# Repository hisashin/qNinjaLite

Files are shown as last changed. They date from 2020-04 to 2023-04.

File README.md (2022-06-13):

# Open Source $50 qLAMP machine qNinja



# $300 Real Time PCR and LAMP machine "[qNinja](https://github.com/hisashin/qNinja)" is also available



## Reference Links
- [qNinja portal](https://qninja.hisa.dev)

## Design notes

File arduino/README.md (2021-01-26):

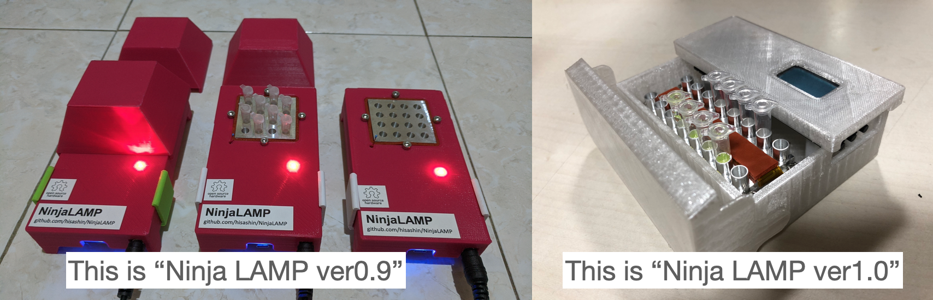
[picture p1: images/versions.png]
versions


The configuration for each version can be found in HardwareConf.cpp and HardwareConf.h.
HardwareConf class has two construction methods for two models:

* ver0.9 (initFirstModel)
* ver1.0 (initLCDModel)

Pins, thermistors, PID constants and some model-specific properties for NinjaLAMP's basic functionalities are defined in HardwareConf::initFirstModel() function.

## ver0.9

ver0.9 has no dedicated user interfaces. It sends values every 250　milliseconds by serial communication.
The values can be plotted by the serial plotter of Arduino IDE. This process is implemented in the loop function.

## ver1.0

In April, ver0.9 was released just after a week of rapid prototyping by @hisashin and @maripo. Now @hisashin upgraded its PCB and 3d model  to ver1.0 with widely used [Seeeduino Xiao](https://wiki.seeedstudio.com/Seeeduino-XIAO/), [I2C SSD1306 LCD](https://www.aliexpress.com/item/33028828291.html?spm=a2g0s.9042311.0.0.26274c4dPiM0Ki), [I2C 2kb EEPROM](https://www.digikey.com/en/products/detail/stmicroelectronics/M24C02-RMN6TP/2038677) and 3 tact switches.
- [Hardware updrade is done (2020 Nov 10)](https://www.facebook.com/hisakawa/posts/10158727487954481)
- [New Package (2020 Nov 6)](https://www.facebook.com/hisakawa/posts/10158717794254481)
- [New PCB (2020 Oct 28)](https://www.facebook.com/hisakawa/posts/10158696375544481)
- [KiCad](https://github.com/hisashin/NinjaLAMP/tree/master/kicad/NinjaLAMP)
- [3d model](https://gallery.autodesk.com/projects/149287/ninjalamp)

NinjaLAMP will get following benefits from this upgrade.

- **Standalone** : No need to be connected to PC anymore. LCD displays all informations and we can choose menu by tapping switches as up/down/ok buttons.
- **Programmable** : We can configure custom temperature profiles with switches and store them in EEPROM.
- **Manufacture Friendly** : PCB supports [Seeed PCBA](https://www.seeedstudio.com/prototype-pcb-assembly.html) service and here is their quotation. All electric parts are included and soldered except $1.66 LCD and $0.46 thermistor. With $10 heater and $10 tube holder, NinjaLAMP can be manufactured less than $40. That's great advantage for screening mass poplulation.

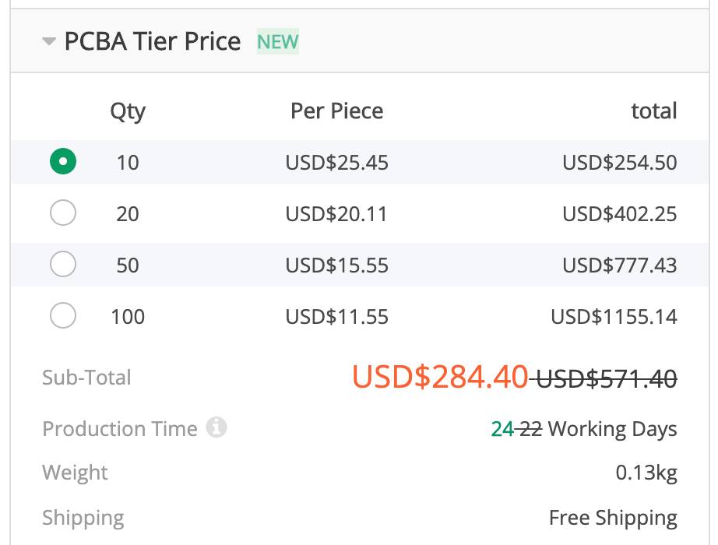
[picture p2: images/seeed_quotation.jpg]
seeed_quotation


### Pin assignment

* LED_R : PA02_A0_D0
* LED_G : PA04_A1_D1
* LED_B : PA10_A2_D2
* HEATER : PA11_A3_D3
* SDA : PA08_A4_D4_SDA
* SCL : PA09_A5_D5_SCL
* AIN_AIR : PB08_A6_D6_TX
* TACT2 : PA06_A10_D10_MOSI
* TACT1 : PA05_A9_D9_MISO
* TACT0 : PA07_A8_D8_SCK
* AIN_WELL : PB09_A7_D7_RX

---

**For Valerio**

## How to Setup IDE and test ver1.0

* Connect NinjaLAMP to your computer with USB TypeC cable. No need to connect 12V AC adapter at first.
* NinjaLAMP ver1.0 uses [Seeeduino XIAO](https://wiki.seeedstudio.com/Seeeduino-XIAO/)(not AVR but SAMD21). Follow their **[Software Step 1 to 5](https://wiki.seeedstudio.com/Seeeduino-XIAO/#software)**
* Upload **"File > Examples > 01.Basics > Blink"** to NinjaLAMP. Orange LED next to USB connector will start blinking.
* Go to **Sketch-> Include Library-> Manage Libraries**, search "ssd1306" and install Alexey Dynda's **[ssd1306 library](https://github.com/lexus2k/ssd1306)**.

* Add "NinjaLAMPCore" library to the build environment. Choose **Sketch > Add .ZIP Library...** and select **NinjaLAMP/arduino/lib/NinjaLAMPCore.zip**.

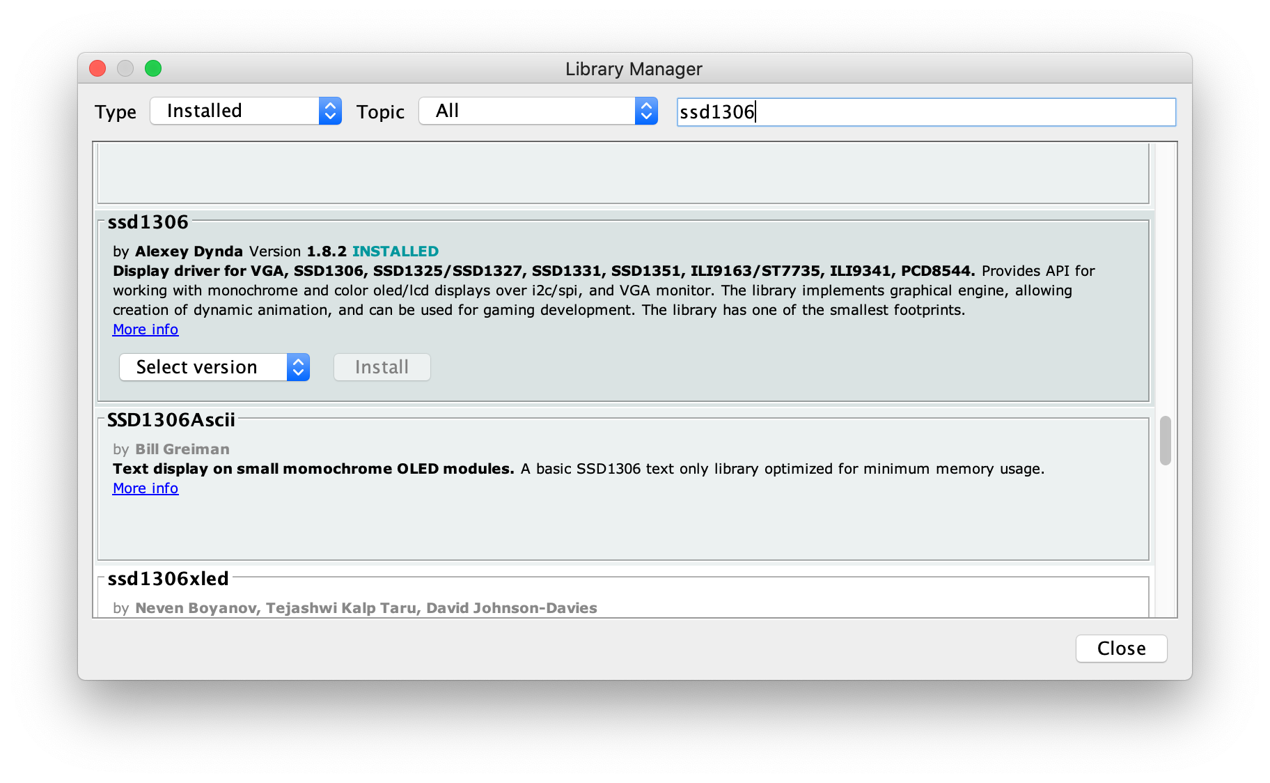
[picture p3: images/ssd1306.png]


* Restart Arduino IDE
* Upload **"File > Examples > ssd1306 > demos > ssd1306_demo"** to NinjaLAMP. I2C LCD displays [demo](https://github.com/lexus2k/ssd1306/blob/master/examples/demos/ssd1306_demo/ssd1306_demo.ino).
* Clone this NinjaLAMP respository to somewhere
* Upload [NinjaLAMP/arduino/examples/xiao_example_gpio](https://github.com/hisashin/NinjaLAMP/tree/master/arduino/examples/xiao_example_gpio)
* Click magnifying glass icon at the top-right corner and set rate to "9600 baud"
* Tap switches to change values. If adapter is connected, tube holder will be heaten. Be careful.

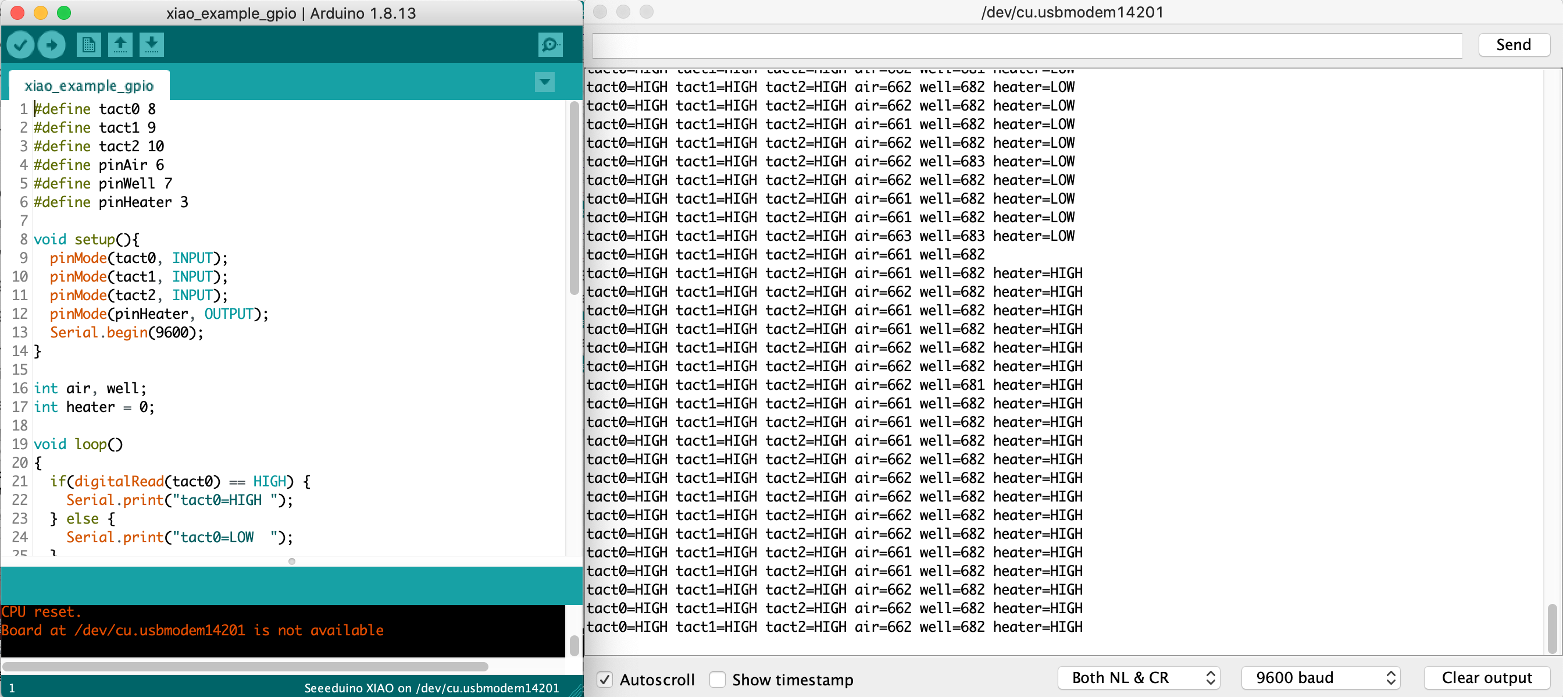
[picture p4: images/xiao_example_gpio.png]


* Upload [NinjaLAMP/arduino/examples/xiao_example_eeprom](https://github.com/hisashin/NinjaLAMP/tree/master/arduino/examples/xiao_example_eeprom)
* Click magnifying glass icon at the top-right corner and set rate to "9600 baud"
* Program writes 0x32(=50) at address 0 of EEPROM on board with writeI2CByte(). Then readI2CByte() read the value of the same address.

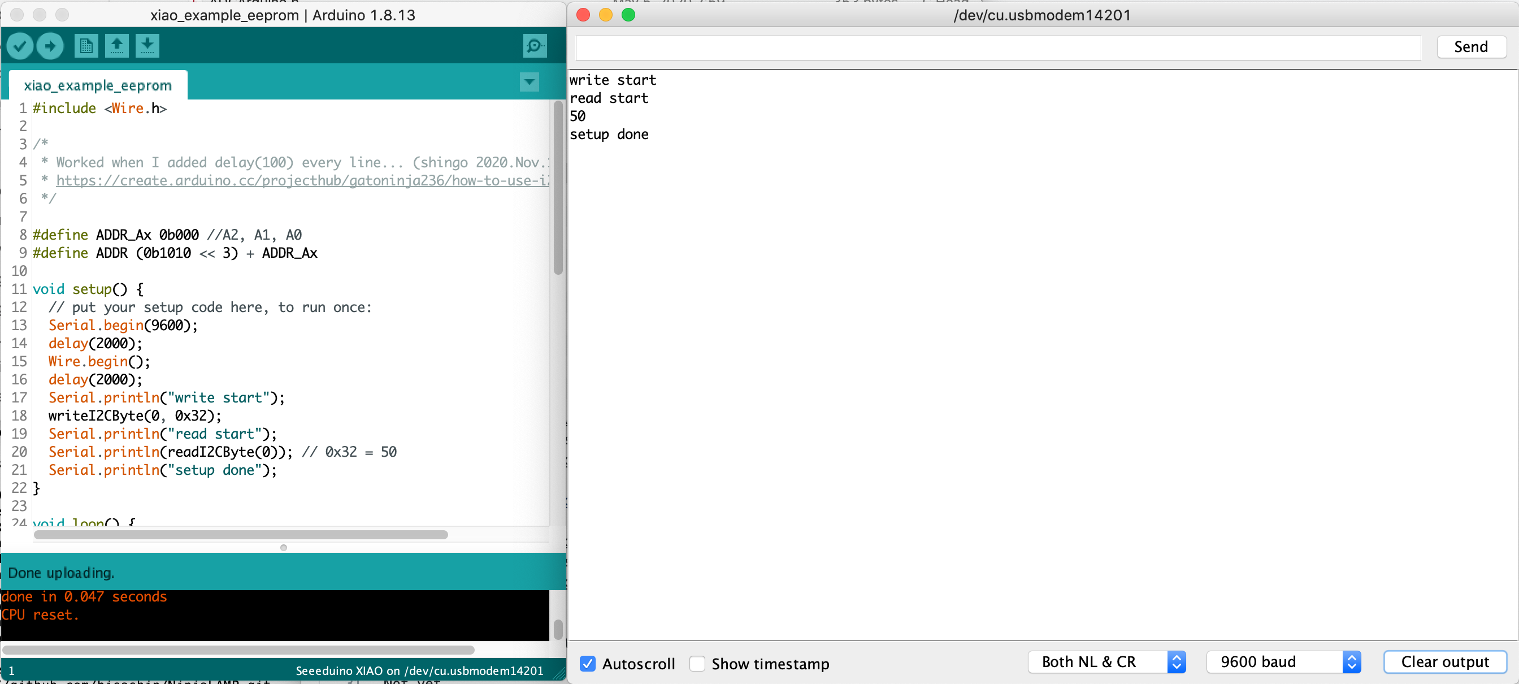
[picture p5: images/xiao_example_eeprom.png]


* Change (address, value) from (0, 0x32) to another. You can confirm its's saved correctly.

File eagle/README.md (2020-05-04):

*Schematic*
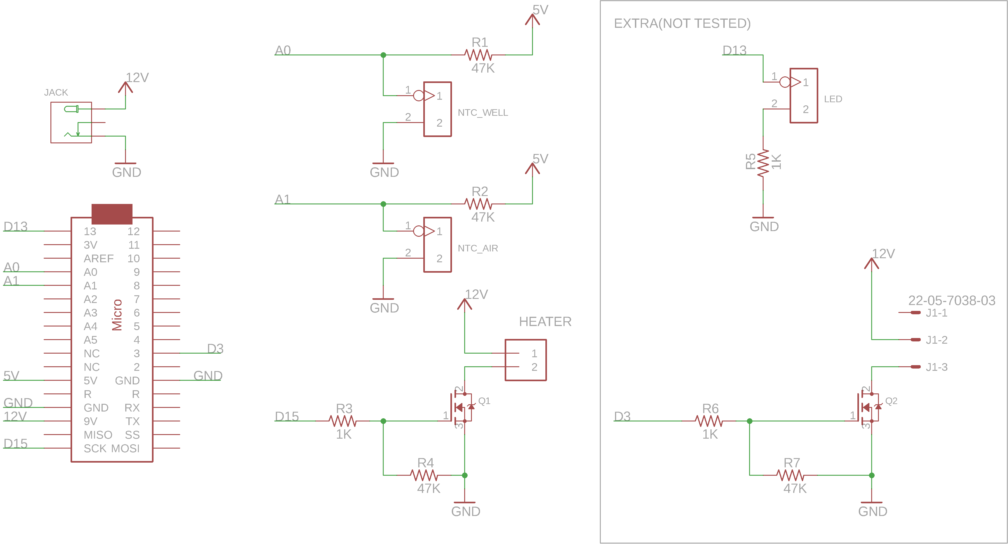
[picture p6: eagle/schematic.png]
Schematic schematic


*Layout for PCB*
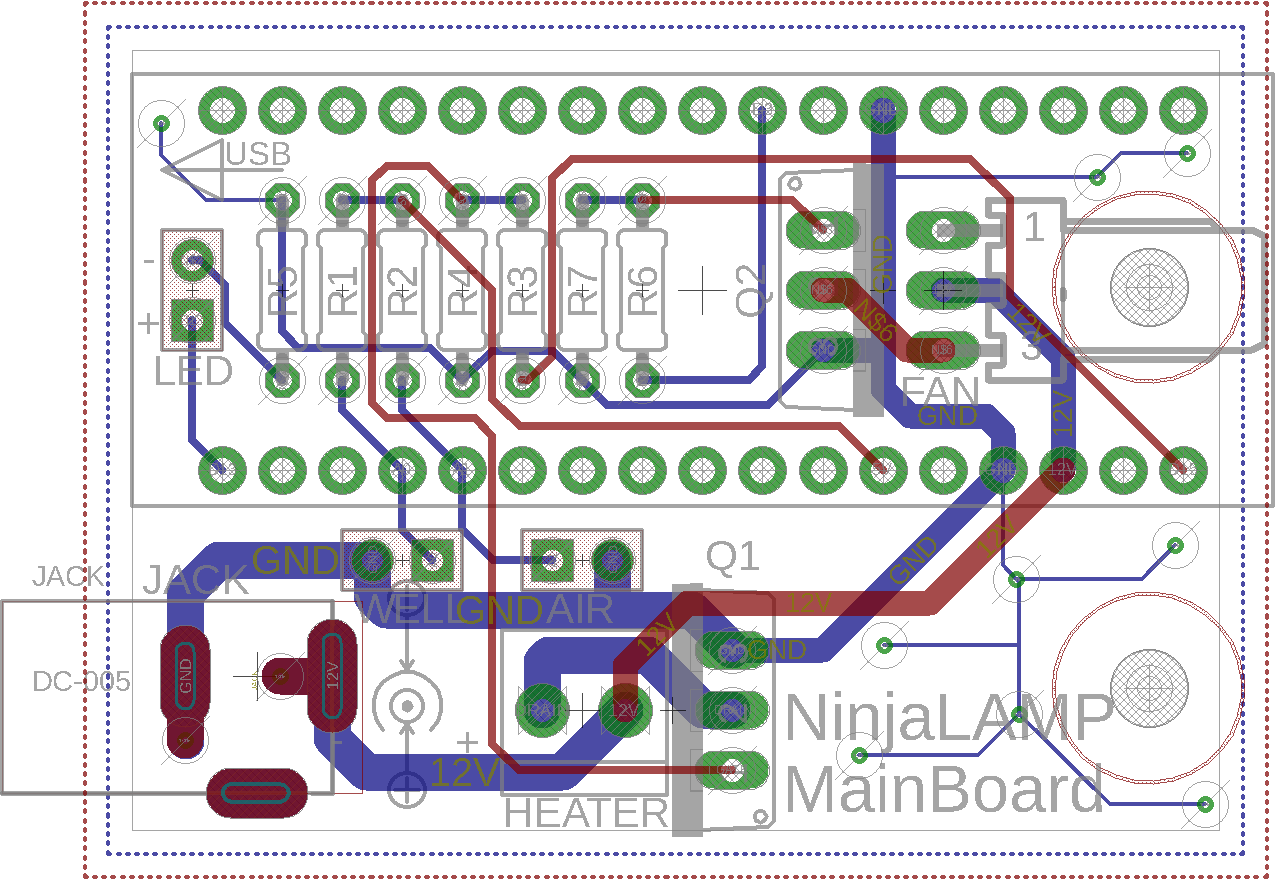
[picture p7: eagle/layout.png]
Layout layout


*Layout for hand wiring*
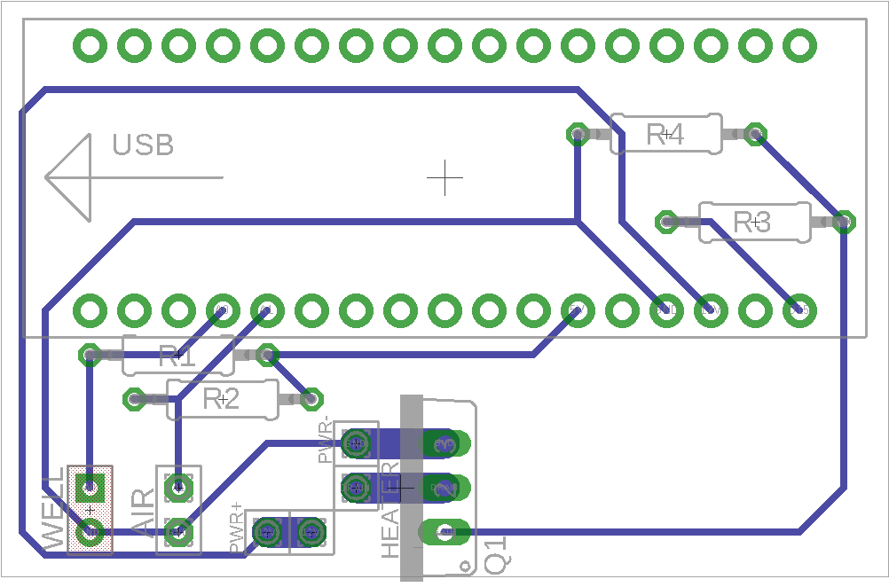
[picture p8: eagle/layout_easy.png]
LayoutEasy layout_easy


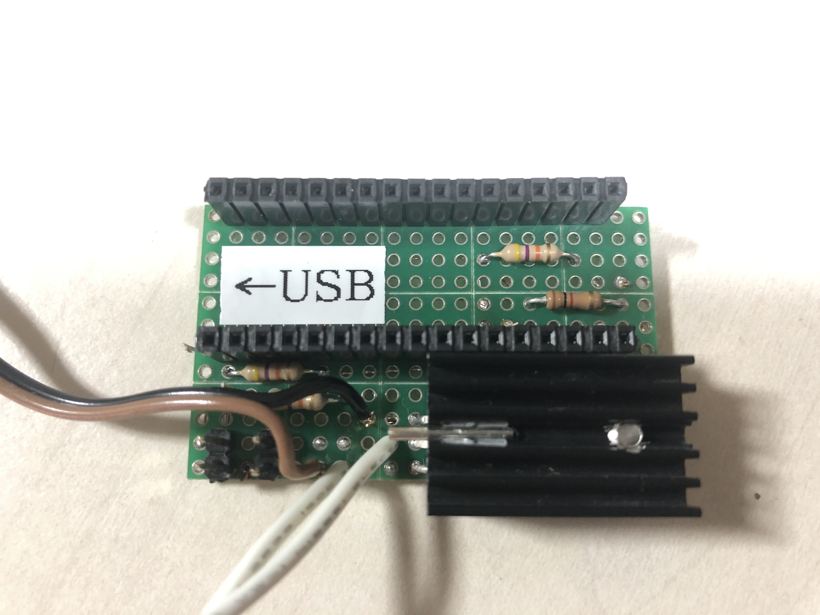
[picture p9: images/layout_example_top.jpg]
hand1

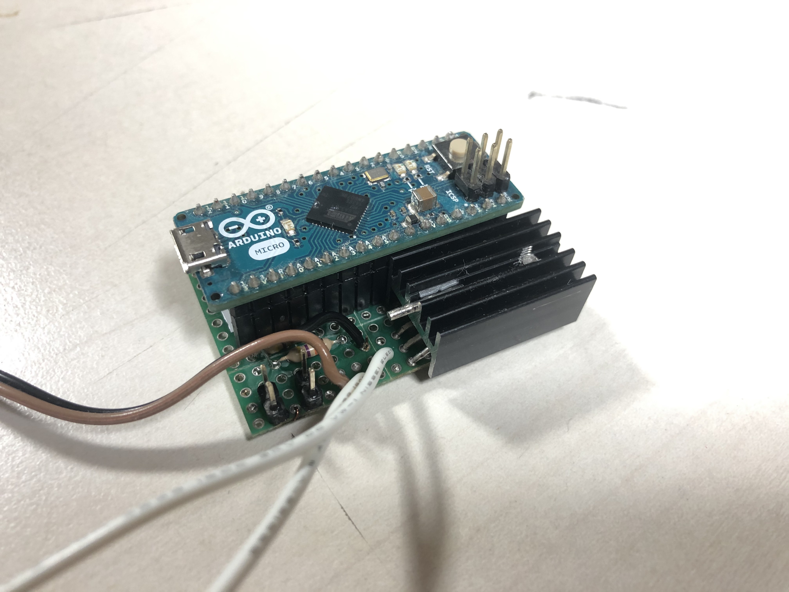
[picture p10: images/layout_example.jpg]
hand2

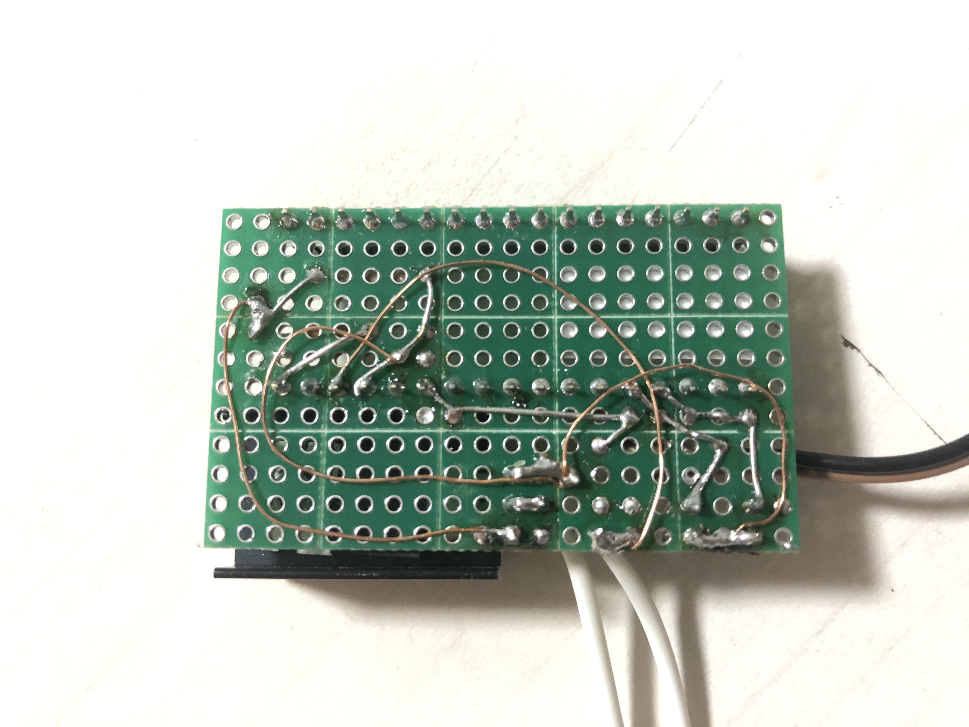
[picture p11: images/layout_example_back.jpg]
hand3


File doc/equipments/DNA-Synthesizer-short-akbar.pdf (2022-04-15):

# OVERVIEW OF DNA PRIMER PRODUCTION LINE

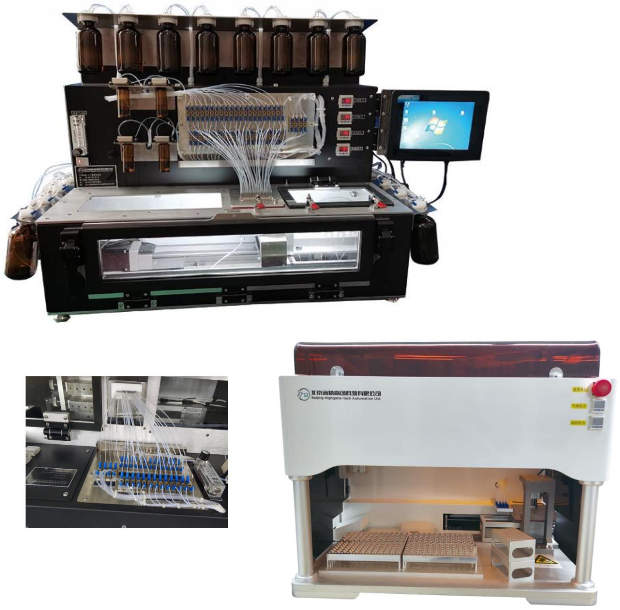
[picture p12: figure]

BY NUR ARKBAR AROFATULLAH, S.P., M.BIOTECH., PH.D.

DNA PRIMER PRODUCTION LINE

DNA primer is single stranded DNA used to prime the polymerase chain reaction. The single stranded DNA is produced synthetically using DNA synthesizer. Typical process used in synthetically creating DNA is the phosphoramidite method. This method is replicated in the 3'- to 5'- direction which is opposite to that in nature on a column containing solid supporting material. The typical solid support for DNA synthesis is Polysterene (PS) and Controlled Phore Glass (CPG). One amidite base is added per synthesis cycle on solid support. When the sequence is completed phosphoramidite, the DNA is separated from the solid support and the base protecting groups are removed. Further post synthesis process is required until the synthetic DNA can be used as PCR primer.

A. THE COMPLETE CYCLE FOR DNA SYNTHESIS INCLUDE:

### 1. Reagent Preparation

Dilution of Phosphoramidite Base Powder to the desired concentration suitable for DNA synthesis. Can be done with dissolver instrument to avoid Oxygen contamination.

### 2. DNA synthesis

a. Detritylation
Detritylation is the removal of protecting (blocking) group Dimethoxytrityl (DMT) from phosphoramidite base. DMT prevent the 5'-end from reacting with anything. Detritylation is typically done with Trichloroacetic Acid (TCA) or Dichloroacetic Acid (DCA) in Dichloromethane. DCA is preferable for longer DNA synthesis due to weaker acid, however the process is slower (60 sec). For faster DNA synthesis (usually shorter DNA), TCA is preferable (35 sec). Longer exposure to acid can cause depurination/mutation.
b. Activation
After DMT is removed, an amidite base (A-C-G-T) is dissolved in Acetonitrile (ACN) and mixed with activator solution Tetrazole or Ethylthiotetrazole (ETT). The activator protonates the 3'-end to facilitate reaction with 5'-end of the oligo.
c. Oligonucleoside coupling on solid support
- Universal solid support: Solid support column with the linker only, without any nucleoside attached.
- Standard support: Solid support with the first nucleoside already attached
d. Capping
To prevent the extension of DNA sequence that did not react in the coupling step, the remaining 5'-hidroxyl group must be blocked with a mixture of two capping solution known as CAP-A (Acetic Anhydride) and CAP-B (N-Methymidazole). This also allows for easier purification in post synthesis
e. Oxidation
The bond of the attached amidite base is strengthened trough iodine oxidation to prepare for the next step of detritylation. Backbone modifications be done as a replacement for the oxidation step.
The Oxidizer:
- Iodine and H2O
- Pyridine
- Tetrahydrofuran
f. Washing
After the oxidation step a wash of Acetonitrile (ACN) is run through the line before the next detritylation. Another wash step is also performed after detritylation.

B. POST DNA SYNTHESIS

Once the DNA sequence is completed, the oligo must undergo post synthesis operation in order to become biologically active
a. Cleavage
The first step to post synthesis is to separate the finished oligo from the solid support. Cleavage is done with strong bases Ammonium Hydroxide, Methylamine, or AMA (a mixture of Ammonium Hydroxide and Methylamine)
b. Deprotection
The second step requires removing the amidite base protecting group from the oligo by raising temperature to 70 – 90 °C.
c. Oligo quantification
- Nanodrop
- Qubit Assays
- Epoch Microplate reader (for batch quantification)
Overview of Post synthesis operation: Cleave + Elute -> Deprotection -> Oligo Quantification
D. PRICE LIST OF REAGENT AND CONSUMABLES FOR DNA SYNTHESIS
No. | Reagents & Consumables | MOQ | Price (USD)
1. | Trichloroacetic Acid (TCA) | 4 Liter | 35
2. | Phosphoramidite base - A/T/G/C | 5 grams | 22.5
3. | Acetonitrile | 4 Liter | 33
4. | Tetrazole or Ethylthiotetrazole | 4 Liter | 106
5. | CAP-A (Acetic Anhydride) | 4 Liter | 82
6. | CAP-B (N-Methymidazole) | 4 Liter | 92.5
7. | Iodine | 4 Liter | 86
8. | Ammonium Hydroxide | 1 Liter | 60
9. Reverse phase silica column - | C18 (price/bag) | 1 bag (100 pcs) | 160
10. CPG column HJ-Z-12-100 | 100nmol (price/bag) | 1 bag (1000 pcs) | 160
11. | Filter | 100 | 160
12. | Molecular trap(10g/piece) | 100 | 950
13. | Molecular trap(5g/piece) | 100 | 785

E. THE REQUIRED MACHINERY FOR PRODUCING DNA PRIMER:
1. Amidites Dissolver Instrument (Step 1)

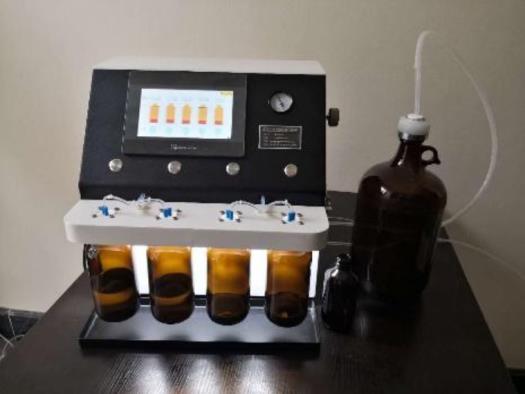
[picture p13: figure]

2. 12 DNA synthesizer (Step 2 a,b,c,d,e, f)

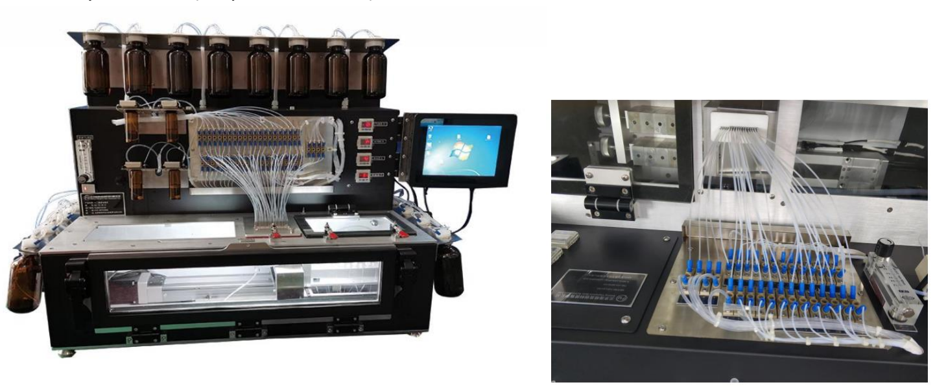
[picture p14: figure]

TECHNICAL SPECIFICATION
No | Parameter | HJ 12-Channel Synthesizer
1. | Synthesis column | 12
2. | Number of amidite inlet | 16
3. | Number of reagent inlet | 7
4. | Synthesis range | 25 nmol – 300 µmol
5. | Synthesis rate | 4-6 Coupling/minutes
6. Total time for 20-unit Poly-T | synthesis | 2 h 30 min
7. Total solvent (acetonitryl) | consumption per coupling | 2.6 mL
8. | Coupling efficiency | 99% (60 base, 50nmol)
9. | CPG feed | CPG in Pre-packed column
10. | Availability of DMT monitoring * | Yes
11. | Production scale (weekdays) | 500-600 primer tube/month
*DMT carbocation absorbs at 495 nm and thereby produces an orange color that can be used to monitor coupling efficiency.

3. Ammonolysis instrument (Step 3 a,b)

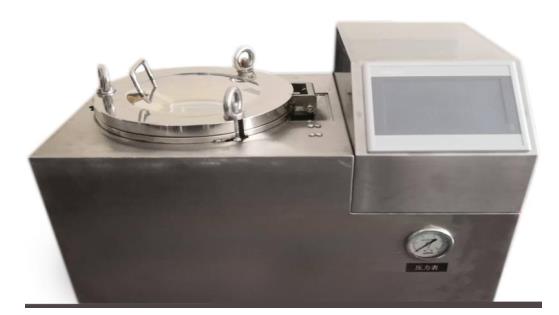
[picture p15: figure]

4. Nanodrop/Qubit/Epoch Microplate reader (Step 3 c)

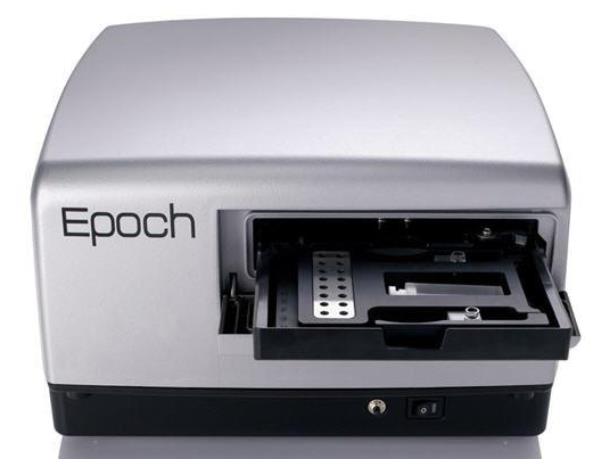
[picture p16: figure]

5. Pipetting workstation (Optional)
The Pipetting workstation with the function of Elution and purification, this workstation uses for different step in the synthesis cycle, because it has different function in one.

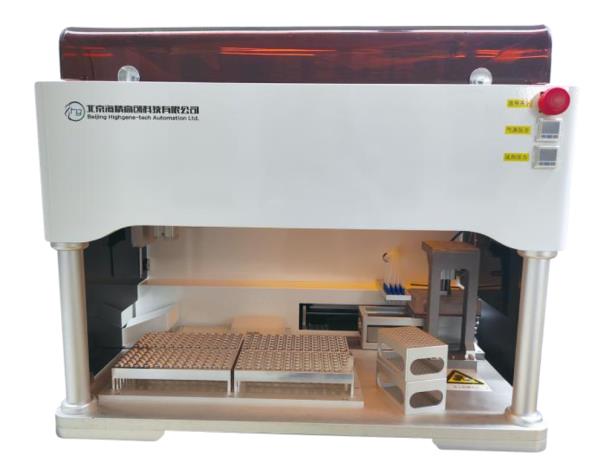
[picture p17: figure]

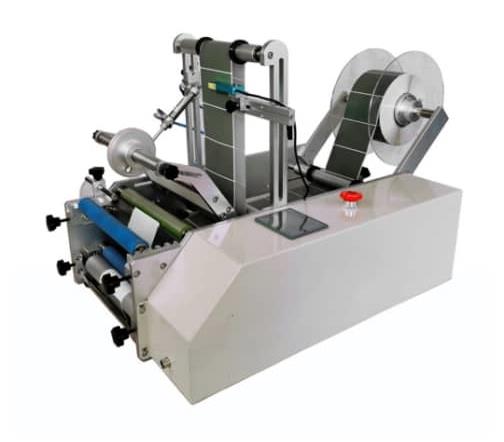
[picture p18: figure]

6. Tube Labeling Machine

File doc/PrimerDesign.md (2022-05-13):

[ApE](https://jorgensen.biology.utah.edu/wayned/ape/) for general primers (and occationall TaqMan probes)

[IDTs quest](https://eu.idtdna.com/pages/tools/primerquest) for qPCR TaqMan assay.

It is basically a cut down and more user friendly version of [Primer3](https://primer3.ut.ee/)

It also provides cheap primers($4 per primer for 25nm) and probes($100).

[NEBs](https://lamp.neb.com/) for LAMP assays

EvaGreen or Sybr Green when using dyes for LAMP or qPCR (if not using probes)

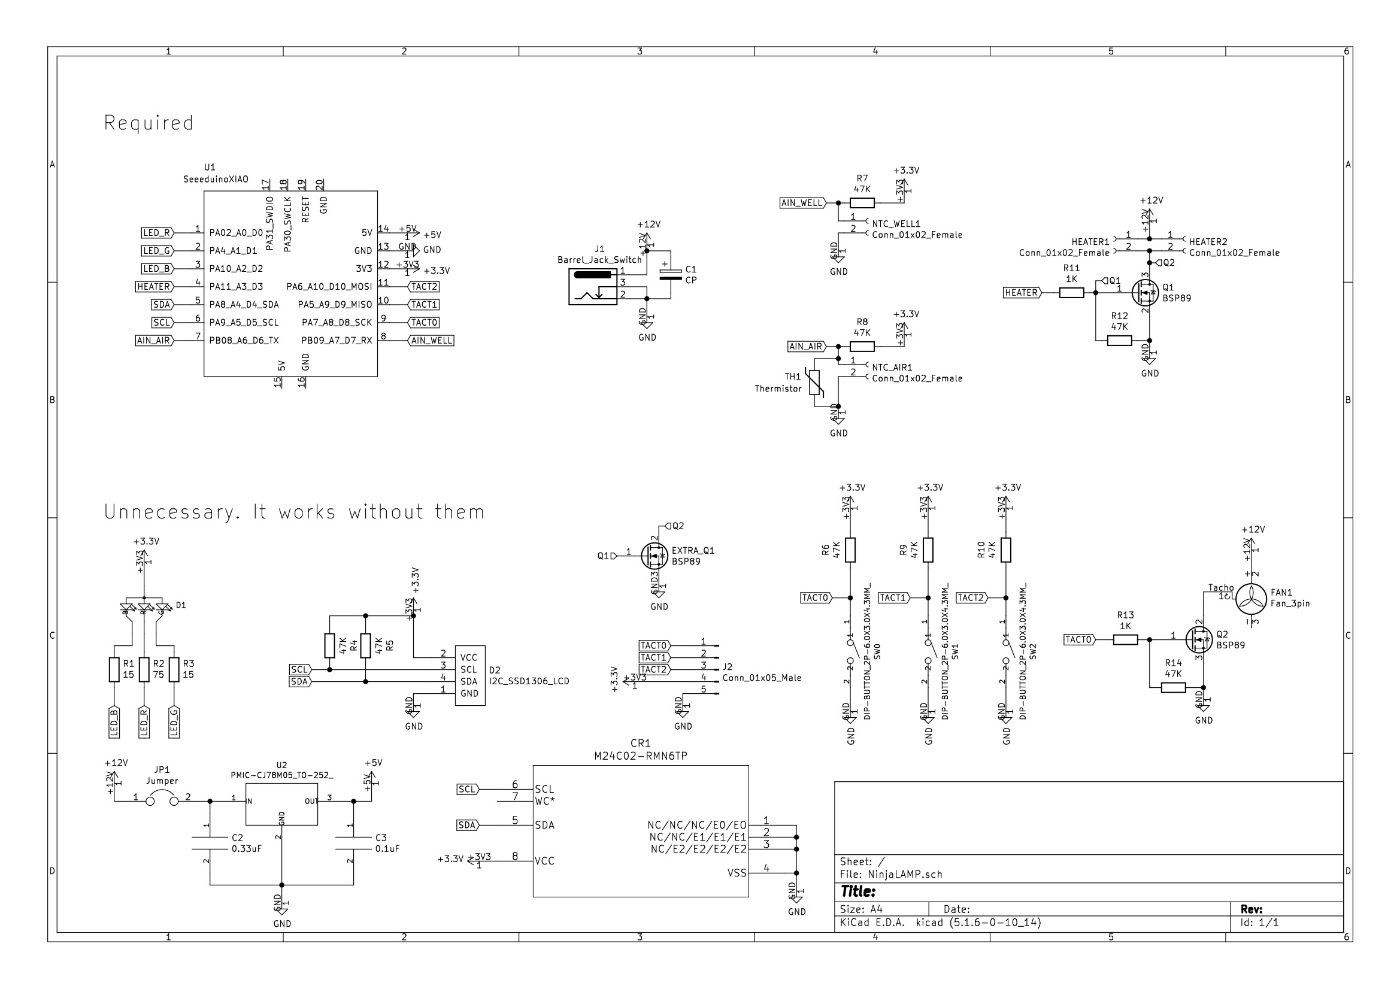
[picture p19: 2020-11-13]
kicad/NinjaLite/ver1.0/schematic.jpeg

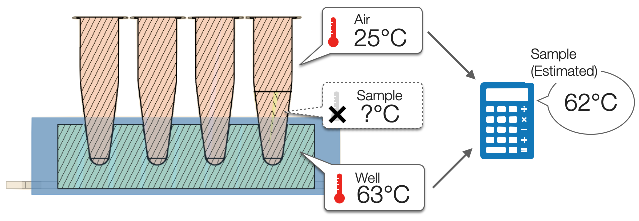
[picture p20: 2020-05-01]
images/heat_simulation/illustration_s.png

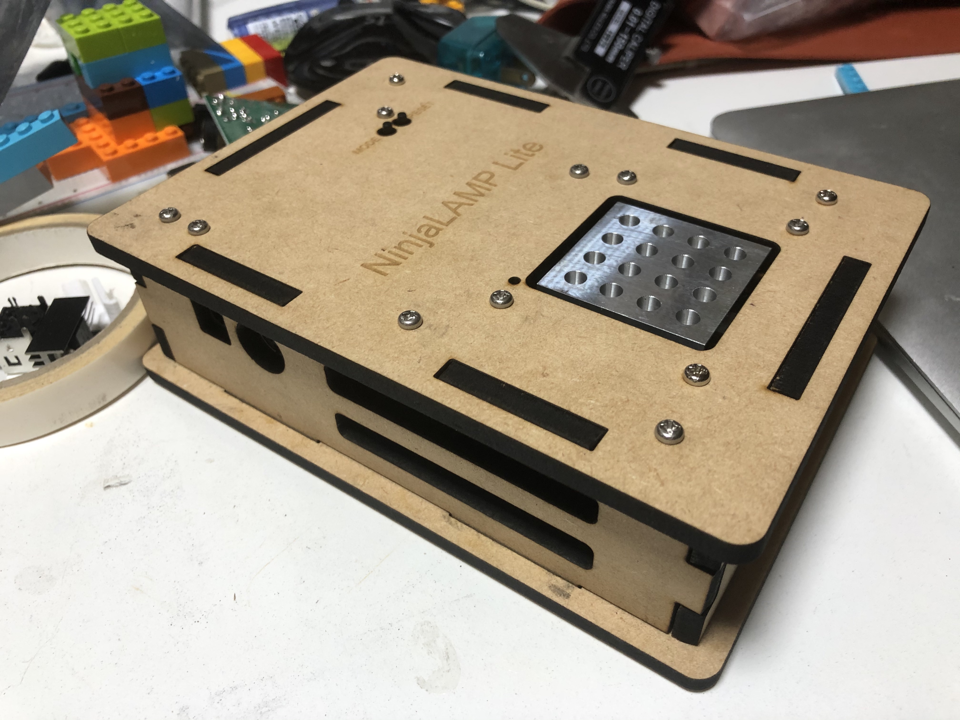
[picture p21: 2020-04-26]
images/lite_outside.jpg

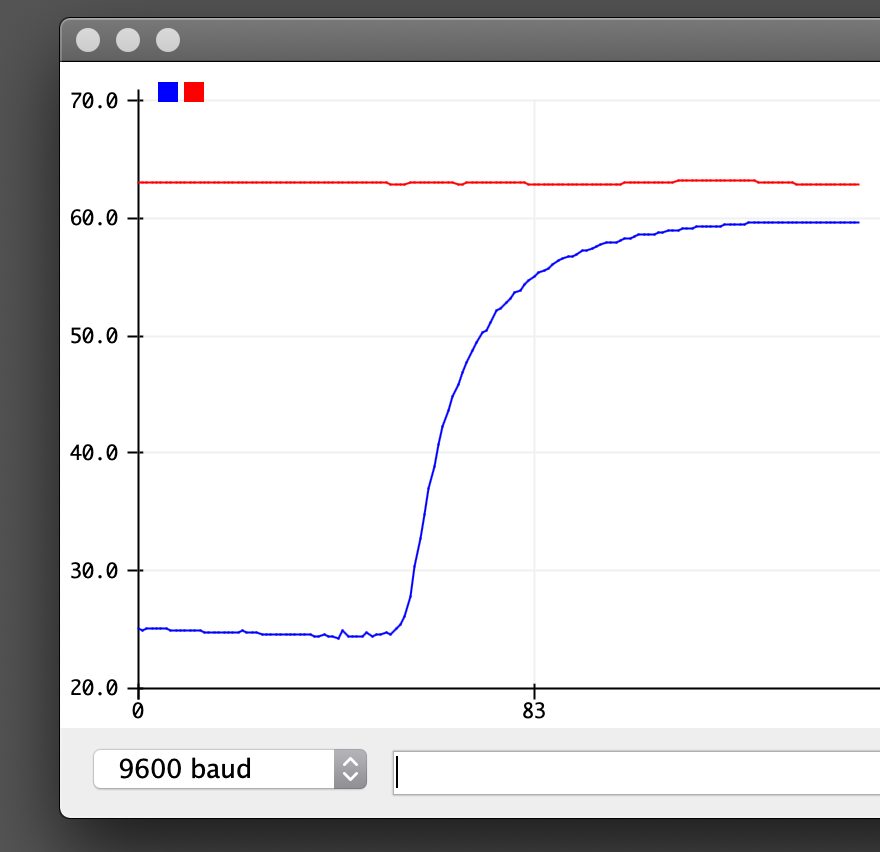
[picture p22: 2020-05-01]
images/heat_simulation/plot_heating.png

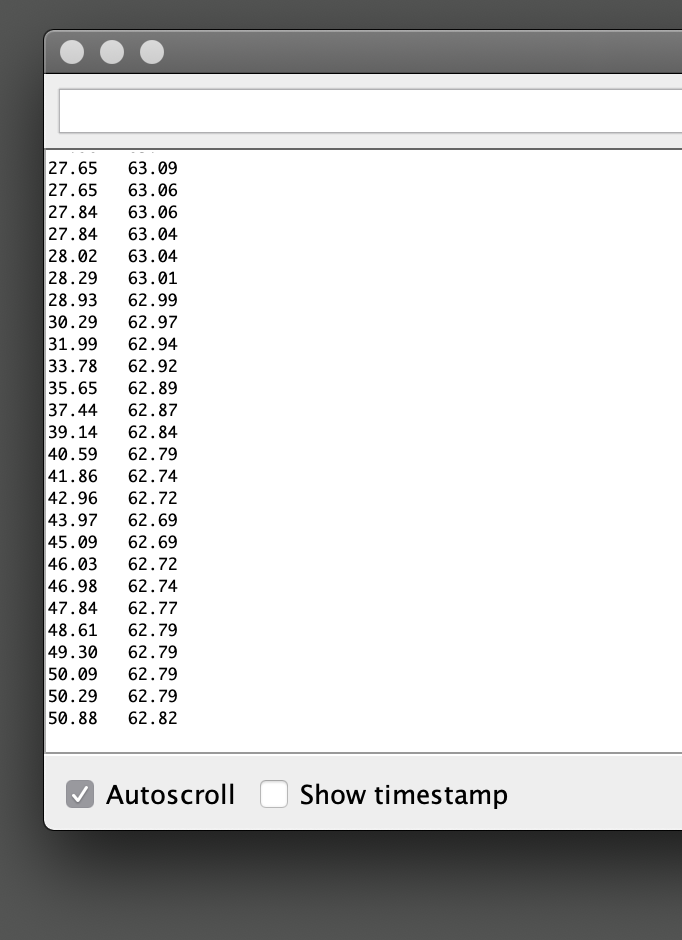
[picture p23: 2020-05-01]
images/heat_simulation/serial_heating.png

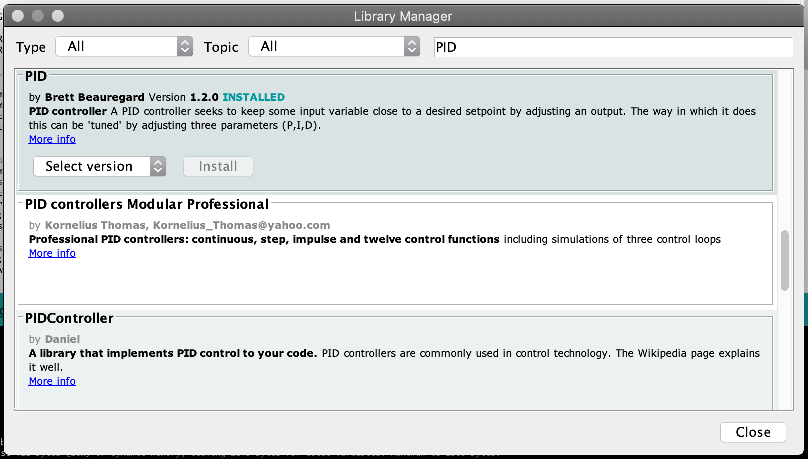
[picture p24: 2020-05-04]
images/arduino_lib_manager.png

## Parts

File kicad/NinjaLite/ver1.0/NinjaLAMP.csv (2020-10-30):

Id | Designator | Package | Quantity | Designation | Supplier and ref
1 | J2 | Pin_Header_Straight_1x05_Pitch1.27mm | 1 | Conn_01x05_Male
2 | D2 | I2C_SSD1306_LCD | 1 | I2C_SSD1306_LCD
3 | D1 | LED4-2.0-D8.0MM | 1 | DIP-LED-RGB-COMMON-ANODE_4P-D8MM_
4 | HEATER1,HEATER2,NTC_AIR1,NTC_WELL1 | Pin_Header_Straight_1x02_Pitch2.54mm | 4 | Conn_01x02_Female
5 | J1 | BarrelJack_Horizontal | 1 | Barrel_Jack_Switch
6 | FAN1 | Molex_KK-6410-03_03x2.54mm_Straight | 1 | Fan_3pin
7 | Q1,Q2 | SOT95P240X112-3N | 2 | BSP89
8 | R4,R5,R7,R8,R12,R9,R14,R6,R10 | R_0603_HandSoldering | 9 | 47K
9 | R11,R13 | R_0603_HandSoldering | 2 | 1K
10 | R1,R3 | R_0603_HandSoldering | 2 | 15
11 | R2 | R_0603_HandSoldering | 1 | 75
12 | U1 | SeeeduinoXIAO-MOUDLE14P-2.54-21X17.8MM | 1 | SeeeduinoXIAO
13 | EXTRA_Q1 | TO-220-3_Vertical | 1 | BSP89
14 | TH1 | R_0603_HandSoldering | 1 | Thermistor
15 | SW1,SW0,SW2 | SW2-5.0-6.0X3.0X4.3MM | 3 | DIP-BUTTON_2P-6.0X3.0X4.3MM_
16 | CR1 | M24C02-RMN6TP | 1 | M24C02-RMN6TP
17 | C2 | C_0603_HandSoldering | 1 | 0.33uF
18 | C3 | C_0603_HandSoldering | 1 | 0.1uF
19 | U2 | TO-252 | 1 | PMIC-CJ78M05_TO-252_
20 | JP1 | SolderJumper-2_P1.3mm_Open_TrianglePad1.0x1.5mm | 1 | Jumper
21 | C1 | ELECTRO-SMD-C-12.5x13.5MM | 1 | CP

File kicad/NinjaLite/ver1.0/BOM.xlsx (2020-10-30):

Designator | Manufacturer Part Number or Seeed SKU | Qty | Link
J1 | 320120003 | 1 | https://statics3.seeedstudio.com/images/opl/datasheet/3410020P1.pdf
Q1 | 305030015 | 1 | https://statics3.seeedstudio.com/images/opl/datasheet/0440200P1.pdf
SW1,SW0,SW2 | 311020025 | 3 | https://statics3.seeedstudio.com/images/opl/datasheet/311020025.pdf
CR1 | M24C02-RMN6TP | 1 | https://file.elecfans.com/web1/M00/9E/F1/o4YBAF1AoEeAb1h6AAt_1Xjtep8324.pdf?filename=o4YBAF1AoEeAb1h6AAt_1Xjtep8324.pdf
C2 | CC0603KRX7R7BB334 | 1 | https://file.elecfans.com/web1/M00/B1/C4/pIYBAF38kjqAET8yABXo2tpxHKE055.pdf?filename=Yageo.pdf
C3 | CL10B104KA8NNNC | 1 | https://file.elecfans.com/web1/M00/5C/4C/o4YBAFt04FWAbe4gAAKwH_HJHDI122.pdf?filename=o4YBAFt04FWAbe4gAAKwH_HJHDI122.pdf
U2 | 310030100 | 1 | https://statics3.seeedstudio.com/images/opl/datasheet/1300040P1.pdf
C1 | 302030098 | 1 | https://statics3.seeedstudio.com/images/opl/datasheet/302030098.pdf
 | 4D03WGJ0473T5E | 2 | https://file.elecfans.com/web1/M00/77/EC/pIYBAFv82zqANTTjAAY2K0EXihA190.pdf?filename=pIYBAFv82zqANTTjAAY2K0EXihA190.pdf
R12 | RC0603FR-0747KL | 1 | https://file.elecfans.com/web1/M00/8C/E1/pIYBAFybLPGAGP4AAA_0AGCR09U105.pdf?filename=GP_Chip+Resistor_Yageo.pdf
R11 | BLM18AG102SN1D | 1 | https://file.elecfans.com/web1/M00/98/3C/pIYBAF0SvoaAcrU3AAOSeBZUswg503.pdf?filename=BLM18_Murata.pdf
NTC_WELL1 | 320020016 | 1 | https://statics3.seeedstudio.com/images/opl/datasheet/320020016.pdf
TH1 | NTCG164KF104FT1S | 1 | https://product.tdk.com/info/en/catalog/datasheets/tpd_automotive_ntc-thermistor_ntcg_en.pdf
U1 | 102010328 | 1 | https://www.seeedstudio.com/Seeeduino-XIAO-Arduino-Microcontroller-SAMD21-Cortex-M0+-p-4426.html

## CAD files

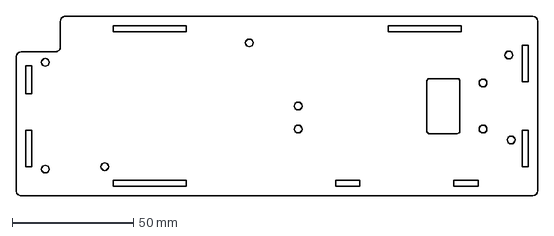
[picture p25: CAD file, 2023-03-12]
cad/2d/dxf-ver0.4/woods_bottom.dxf
214.9 x 74.0 mm

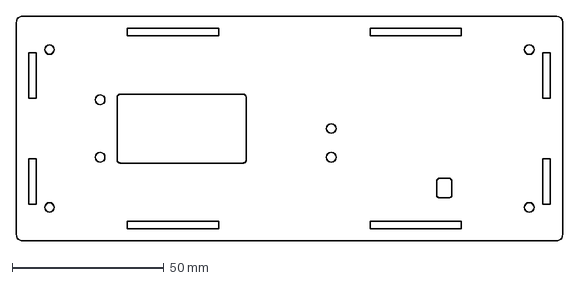
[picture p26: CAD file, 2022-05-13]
cad/2d/dxf/t2.5/body_bottom.dxf
179.9 x 74.0 mm

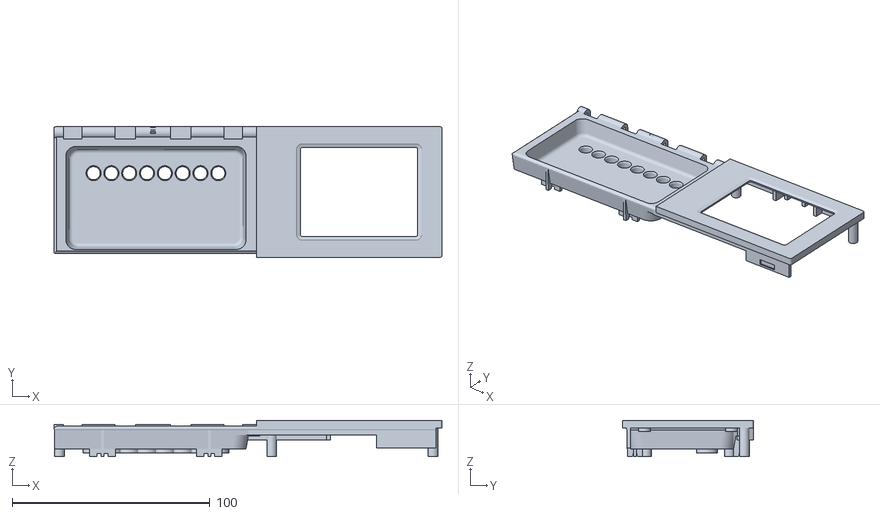
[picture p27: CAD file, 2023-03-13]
cad/3d/stl-ver0.4/3dprint/innerCase_1x8.stl
196.0 x 66.0 x 18.4

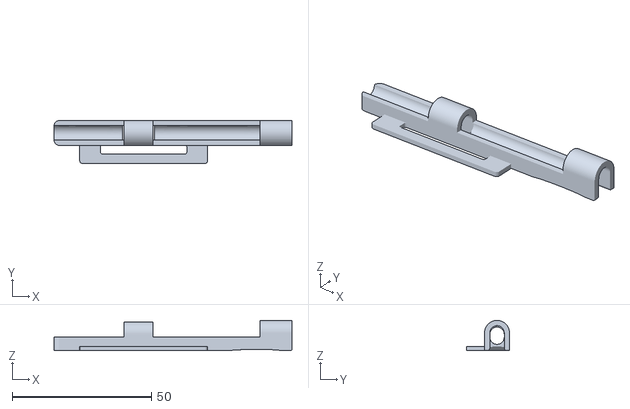
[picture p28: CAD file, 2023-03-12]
cad/3d/stl-ver0.4/ver1.0_PrintMeUpsideDown(b4offsetZ0.5x0.5+X50).stl
85.6 x 15.5 x 10.9

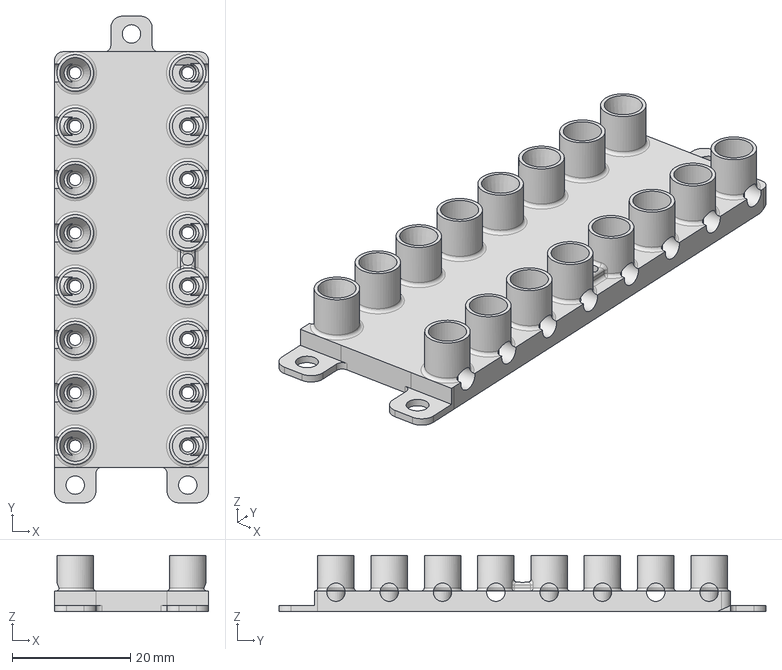
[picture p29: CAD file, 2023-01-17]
cad/3d/tube_holder_210806_2x8 v72.step
26.0 x 82.2 x 9.50 mm

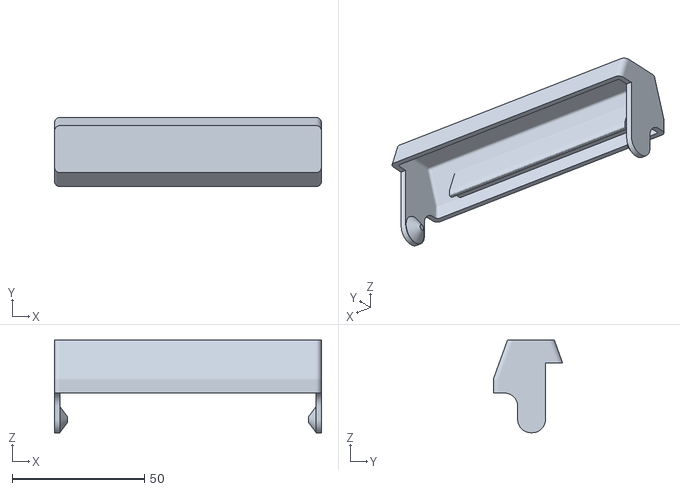
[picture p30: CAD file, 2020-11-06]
cad/3d/ver1.0/1x8/3dprint_1x8_cover.stl
101.0 x 26.2 x 35.0

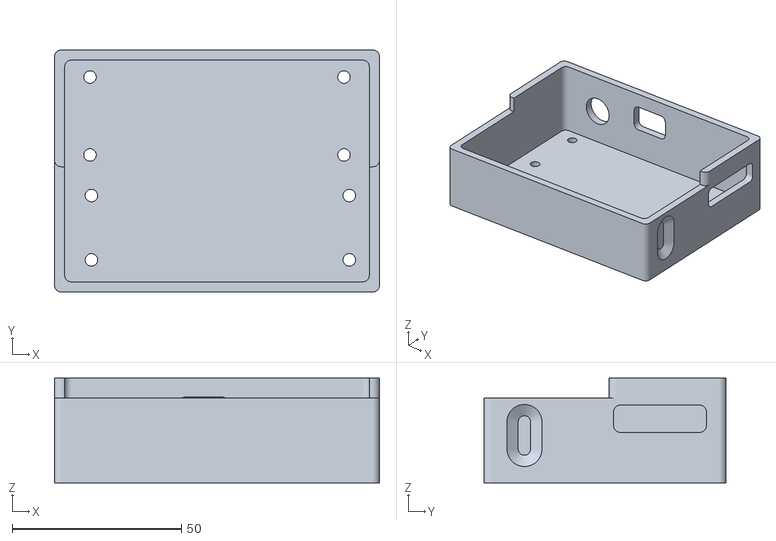
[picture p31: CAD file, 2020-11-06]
cad/3d/ver1.0/2x8/3dprint_2x8_bottom.stl
96.0 x 71.5 x 30.9

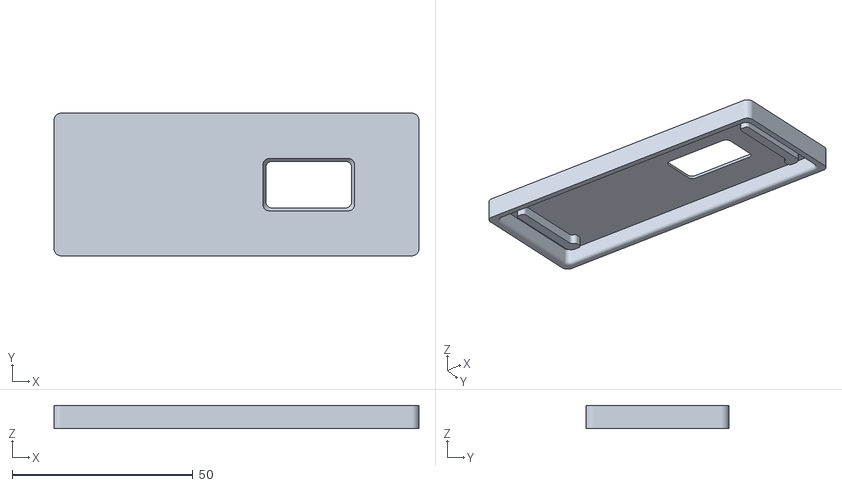
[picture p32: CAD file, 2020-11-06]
cad/3d/ver1.0/4x4/3dprint_top.stl
101.0 x 39.5 x 6.44

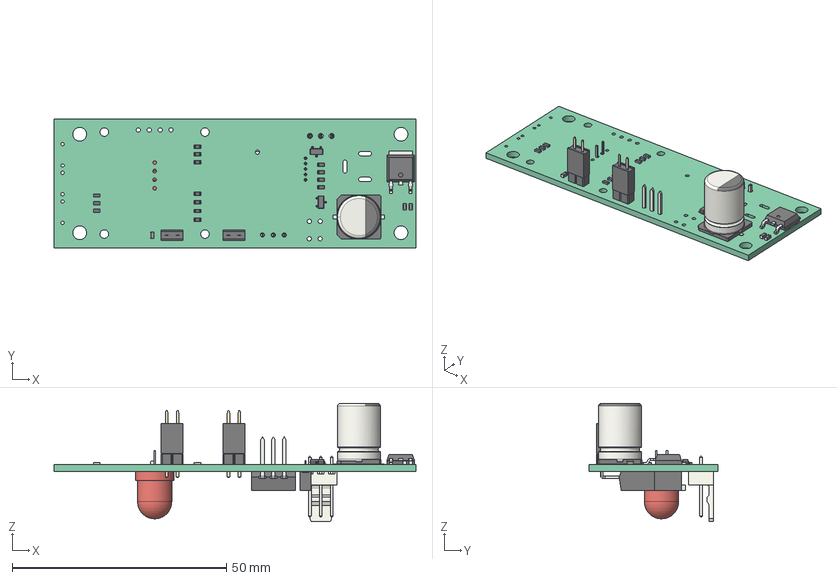
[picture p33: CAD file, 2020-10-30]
kicad/NinjaLite/ver1.0/NinjaLAMP.step
84.5 x 30.0 x 27.6 mm
Local_CS_394c
Pcb_394c
PCB_Sketch_394c
NTC_AIR1_PinHeader_1x02_P254mm_Vertical_5FA54BA2[2]
NTC_AIR1_PinSocket_1x02_P254mm_Vertical_5FA54BA2[3]
NTC_WELL1_AIR1_PinHeader_1x02_P254mm_Vertical_5FA54BB8[2]
NTC_WELL1_AIR1_PinSocket_1x02_P254mm_Vertical_5FA54BB8[3]
Q1_SOT_23_5FA54BDB
Q2_SOT_23_5FC62037
R4_R_0603_1608Metric_5FA5EEA7[2]
R5_R_0603_1608Metric_5FA5EE77[2]
R7_R_0603_1608Metric_5FA54C48[2]
R8_R_0603_1608Metric_5FA54C59[2]
R11_R_0603_1608Metric_5FB015A9[2]
R12_R_0603_1608Metric_5FA54C7B[2]
R9_R_0603_1608Metric_5FBBD0C3[2]
R1_R_0603_1608Metric_5FA54C9D[2]
R2_R_0603_1608Metric_5F9A590A[2]
R13_R_0603_1608Metric_5FC622F6[2]
R3_R_0603_1608Metric_5FA54CD0[2]
R14_R_0603_1608Metric_5FC62217[2]
TH1_C_0603_1608Metric_5FD6973E[2]
R6_R_0603_1608Metric_5F9A13DC[2]
R10_R_0603_1608Metric_5F9A13ED[2]
C2_C_0603_1608Metric_5FBC6DB6[2]
C3_C_0603_1608Metric_5FBC6A8D[2]
U2_TO_252_2_5FBC6AF2
C1_CP_Elec_10x143_5FBC6B8C
J2_PinSocket_1x05_P127mm_Vertical_5FD4DE27[2]
FAN1_Molex_AE_6410_03A_5FD73072[2]
EXTRA_Q1_TO-220-3_Horizontal_TabUp_5FB01CE5[2]
D1_LED_D8.0mm_5F98D6B4

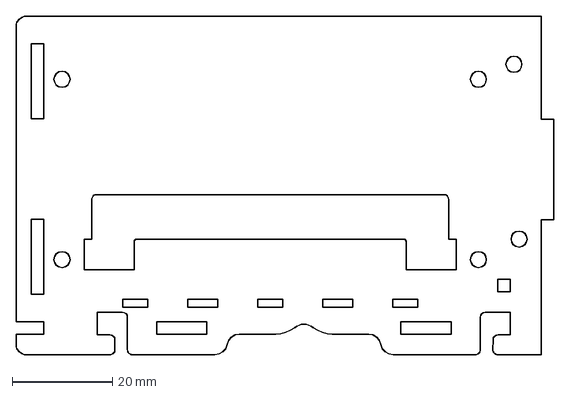
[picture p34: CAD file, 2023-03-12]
cad/2d/dxf-ver0.4/woods_topA_1x8.dxf
107.4 x 67.6 mm

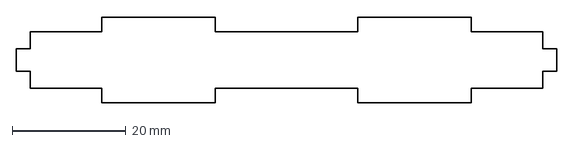
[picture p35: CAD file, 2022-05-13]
cad/2d/dxf/t2.5/lid_front.dxf
95.0 x 15.0 mm

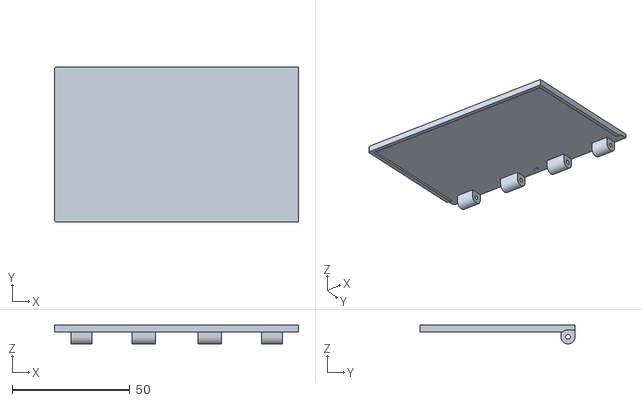
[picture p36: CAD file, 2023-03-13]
cad/3d/stl-ver0.4/3dprint/lid.stl
103.8 x 66.0 x 8.00

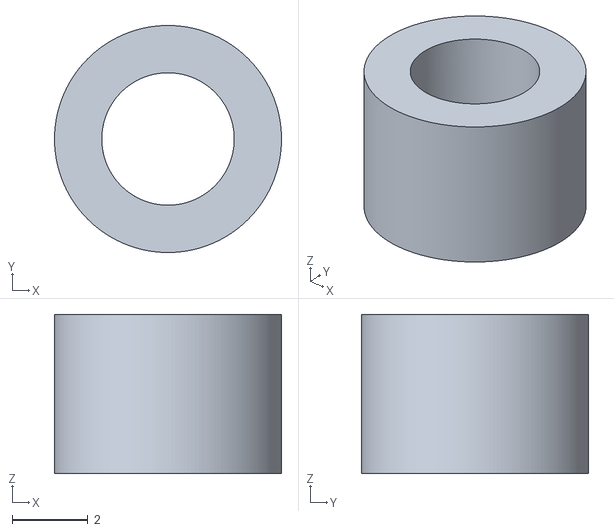
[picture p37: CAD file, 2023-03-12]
cad/3d/stl-ver0.4/footer.stl
6.00 x 6.00 x 4.22

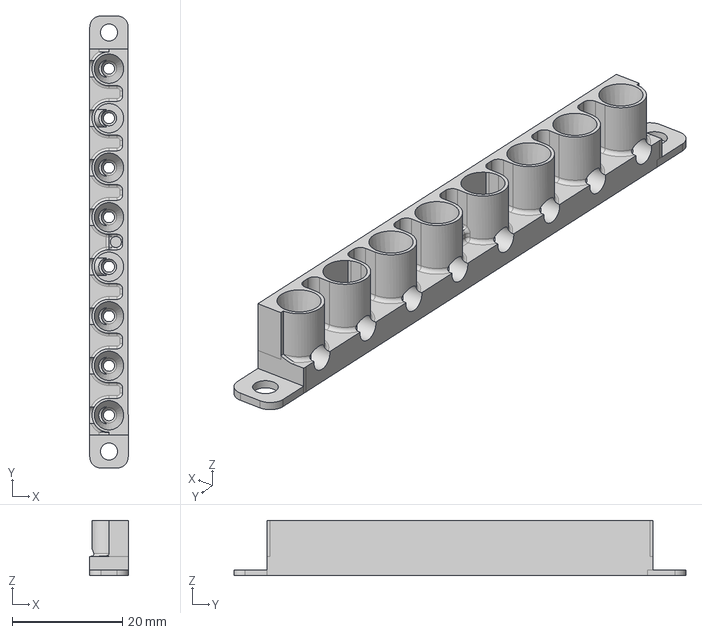
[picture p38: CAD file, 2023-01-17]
cad/3d/tube_holder_220302_1x8 v13.step
7.00 x 82.2 x 10.0 mm

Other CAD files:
cad/3d/ver1.0/1x8/3dprint_1x8_bottom.stl
cad/3d/ver1.0/4x4/aluminiumCNC_tube_holder_4x4_a1001-ver3.iges
cad/2d/dxf-ver0.4/woods_lid_holder_x2.dxf
cad/2d/dxf-ver0.2/t1.5/1x8_body_top.dxf
cad/2d/dxf-ver0.2/t1.5/1x8_pcb_south.dxf
cad/2d/dxf-ver0.2/t1.5/2x8_body_top.dxf
cad/2d/dxf-ver0.2/t1.5/body_back.dxf
cad/2d/dxf-ver0.2/t1.5/body_bottom.dxf
cad/2d/dxf-ver0.2/t1.5/body_front.dxf
cad/2d/dxf-ver0.2/t1.5/body_left.dxf
cad/2d/dxf-ver0.2/t1.5/body_right.dxf
cad/2d/dxf-ver0.2/t1.5/lid_back.dxf
cad/2d/dxf-ver0.2/t1.5/lid_bottom.dxf
cad/2d/dxf-ver0.2/t1.5/lid_front.dxf
cad/2d/dxf-ver0.2/t1.5/lid_left.dxf
cad/2d/dxf-ver0.2/t1.5/lid_right.dxf
cad/2d/dxf-ver0.2/t1.5/lid_top.dxf
cad/2d/dxf-ver0.2/t2.5/woods_back.dxf
cad/2d/dxf-ver0.2/t2.5/woods_bottom.dxf
cad/2d/dxf-ver0.2/t2.5/woods_front.dxf
cad/2d/dxf-ver0.2/t2.5/woods_left.dxf
cad/2d/dxf-ver0.2/t2.5/woods_lid_back.dxf
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

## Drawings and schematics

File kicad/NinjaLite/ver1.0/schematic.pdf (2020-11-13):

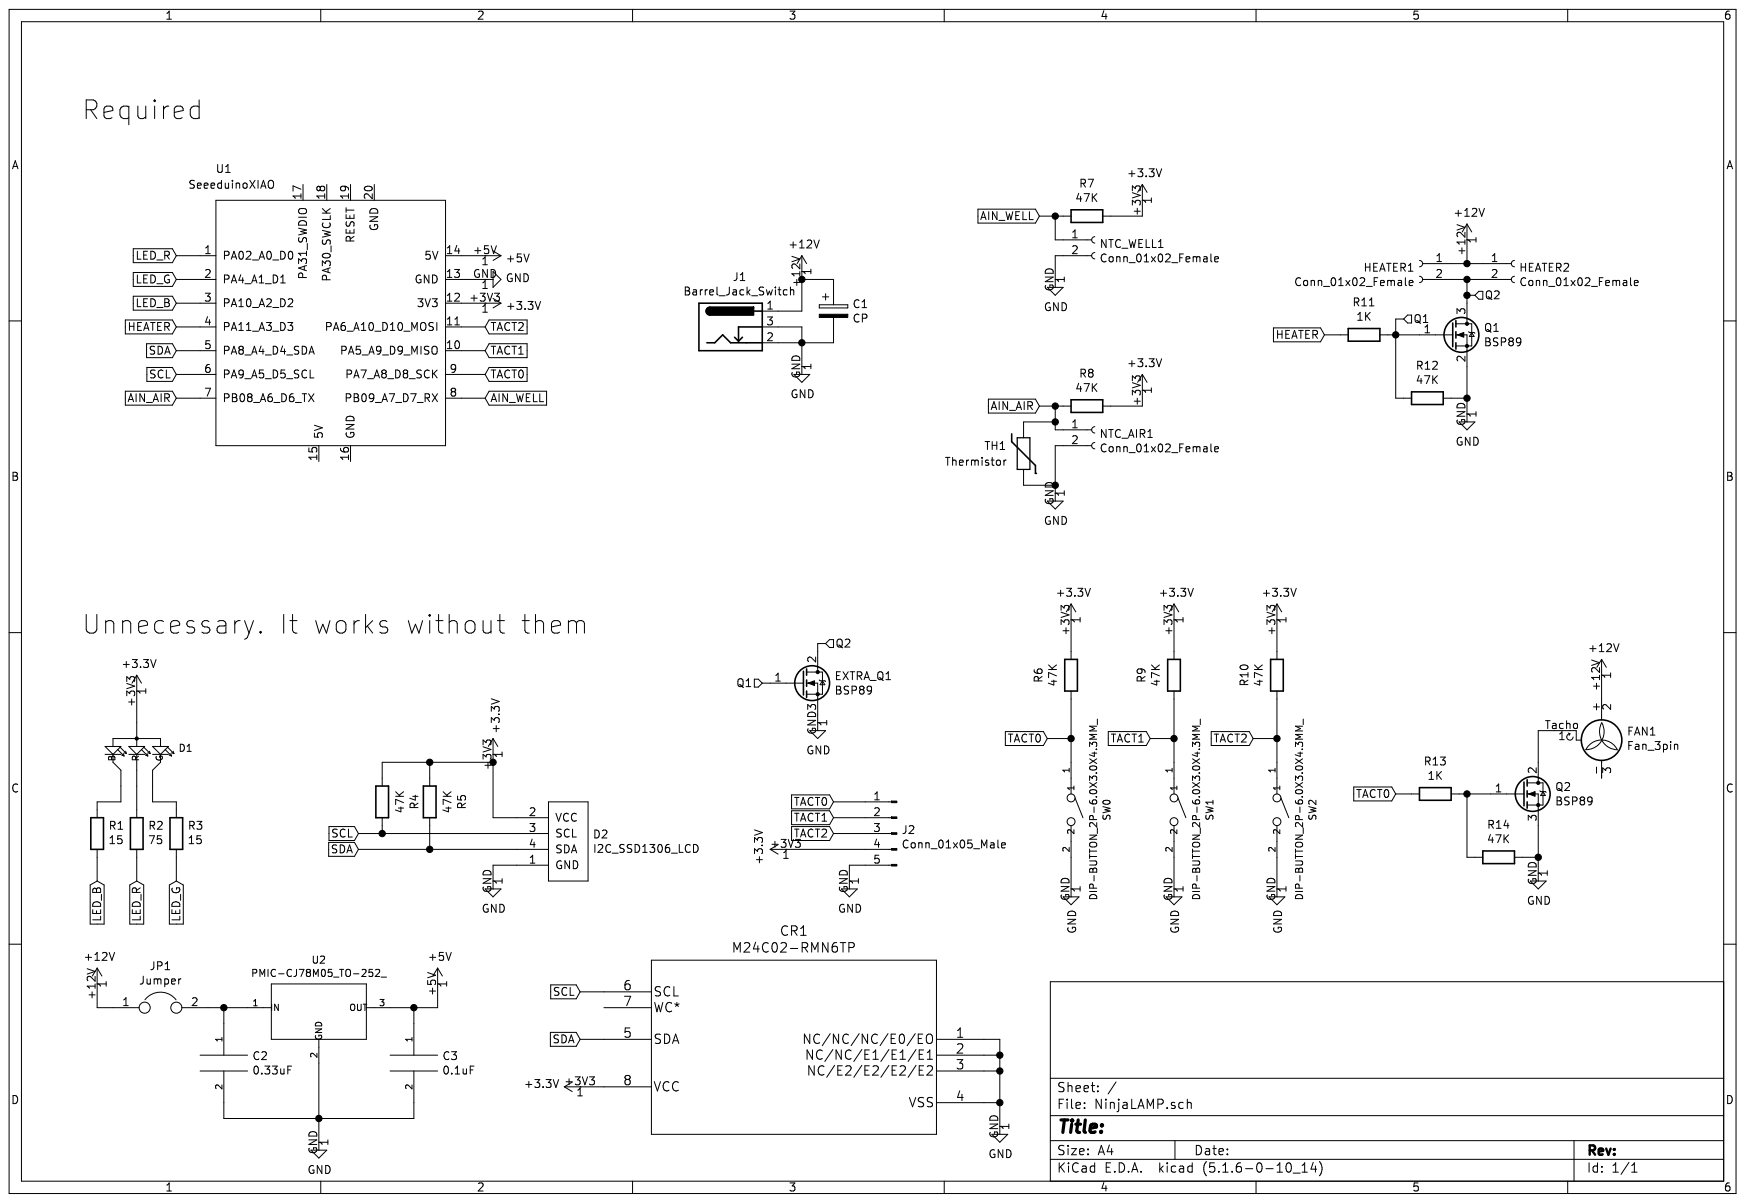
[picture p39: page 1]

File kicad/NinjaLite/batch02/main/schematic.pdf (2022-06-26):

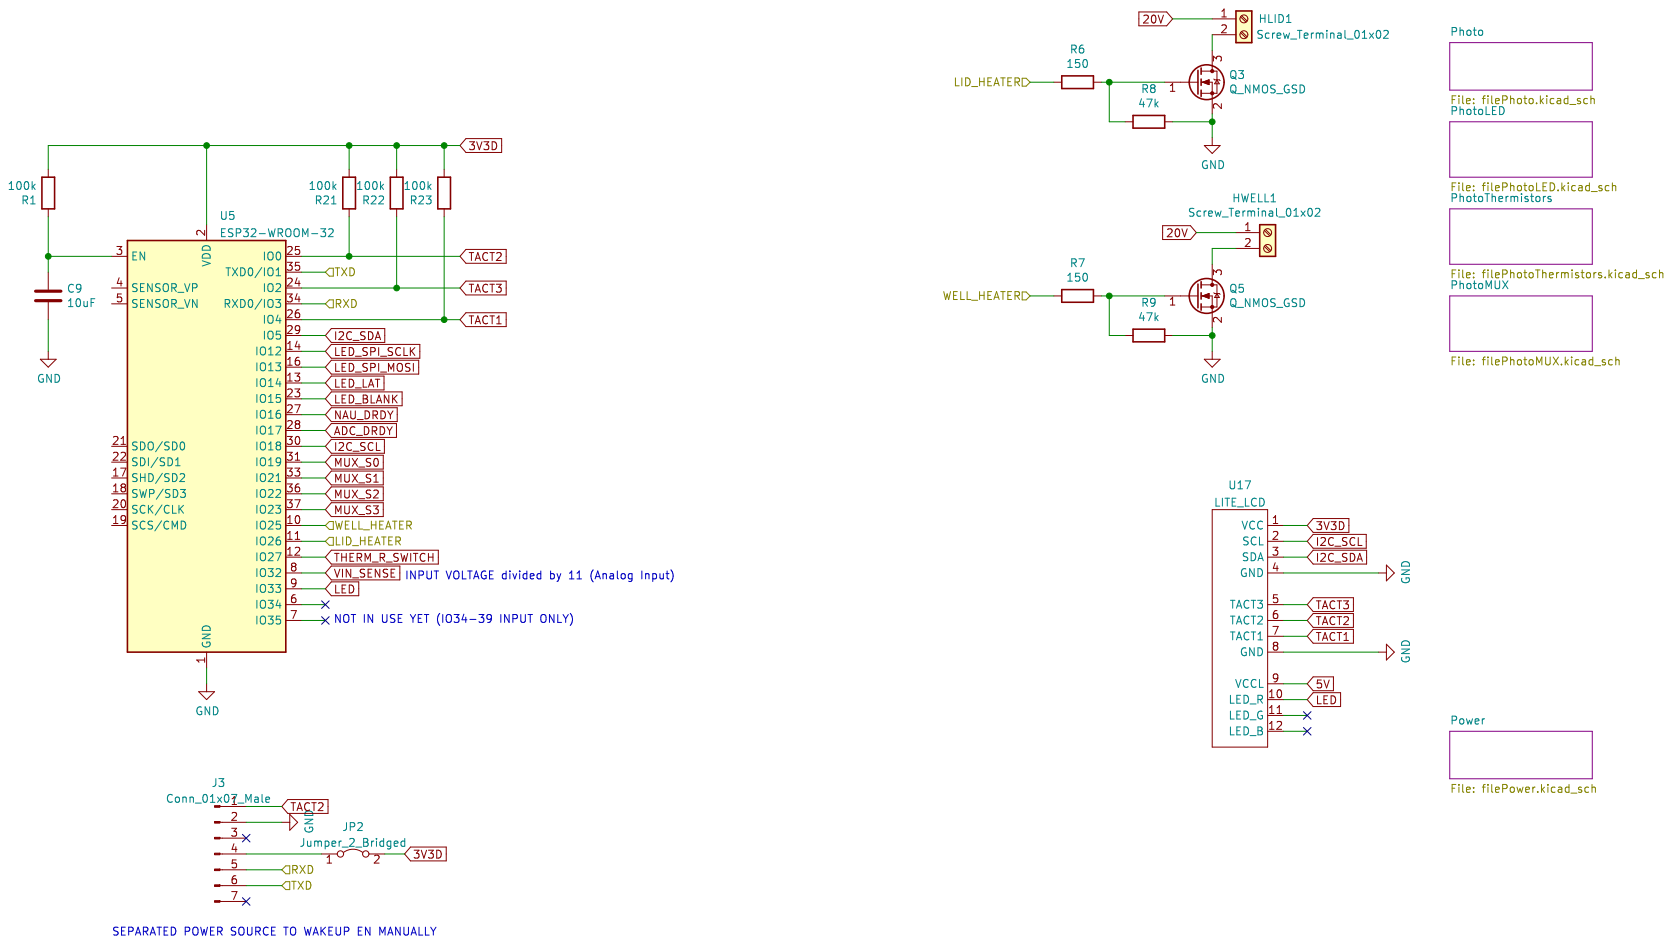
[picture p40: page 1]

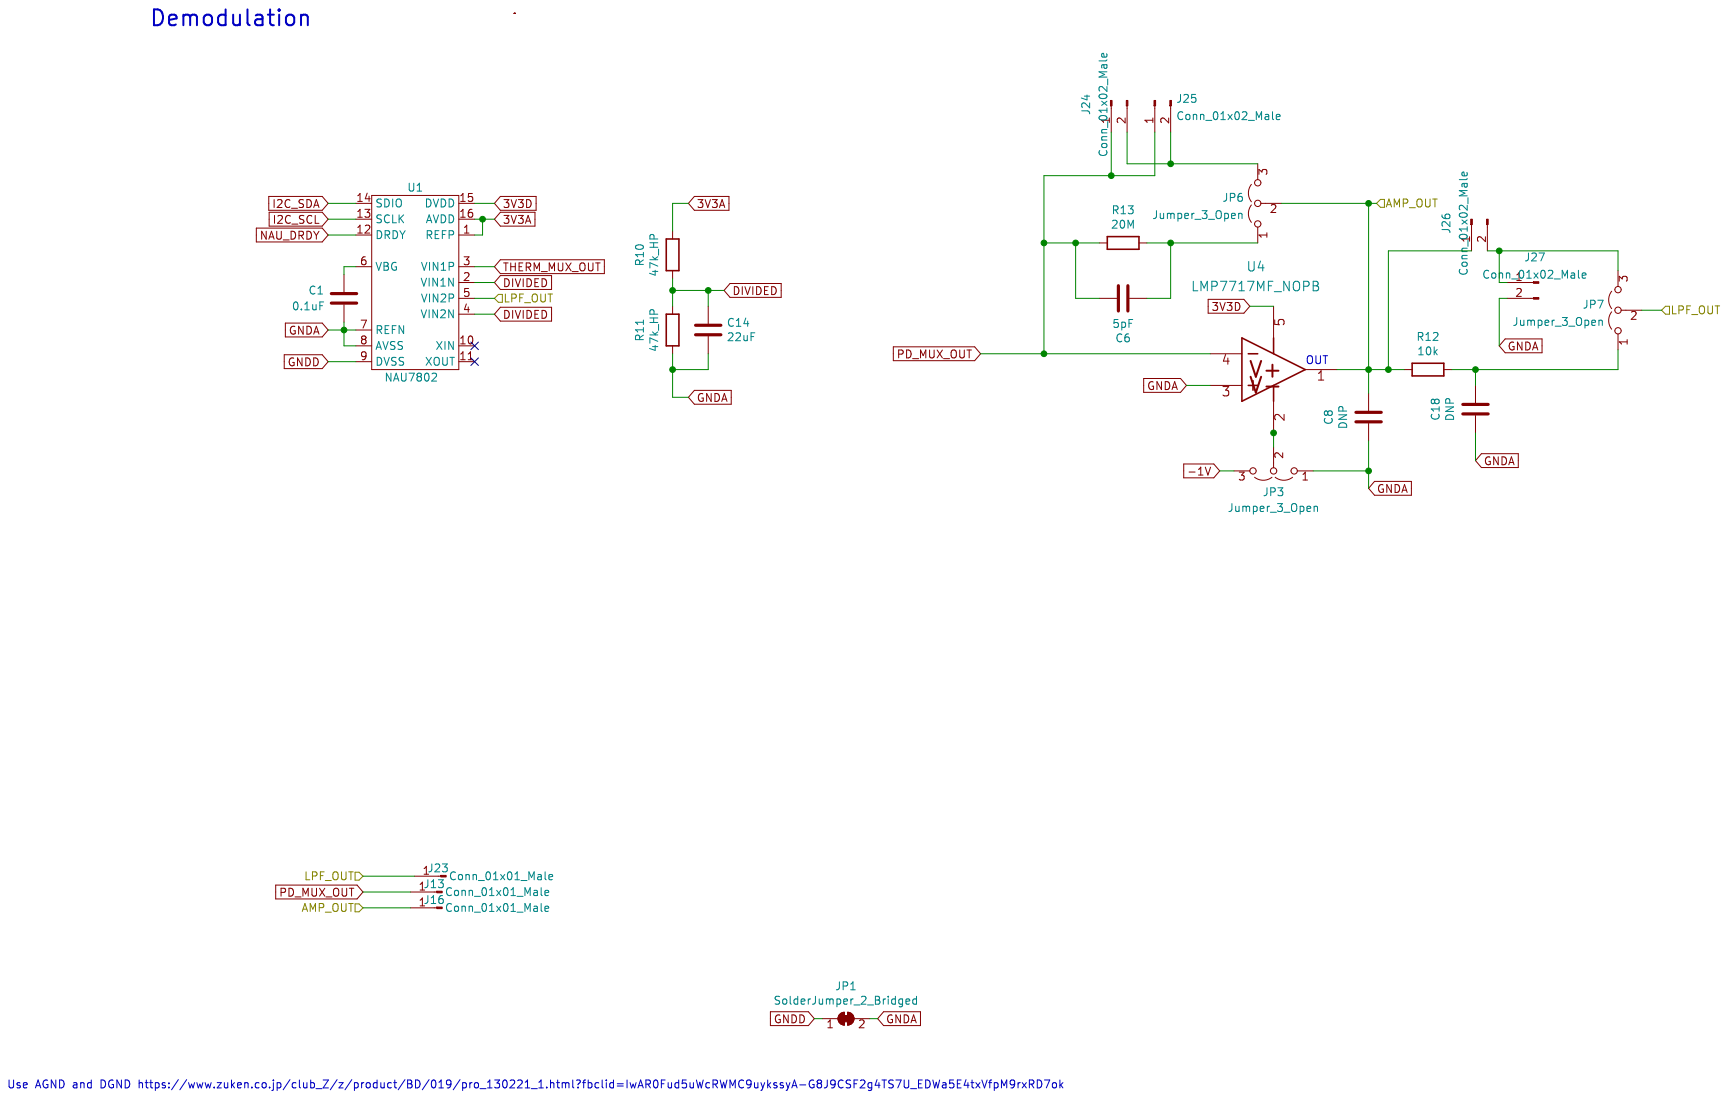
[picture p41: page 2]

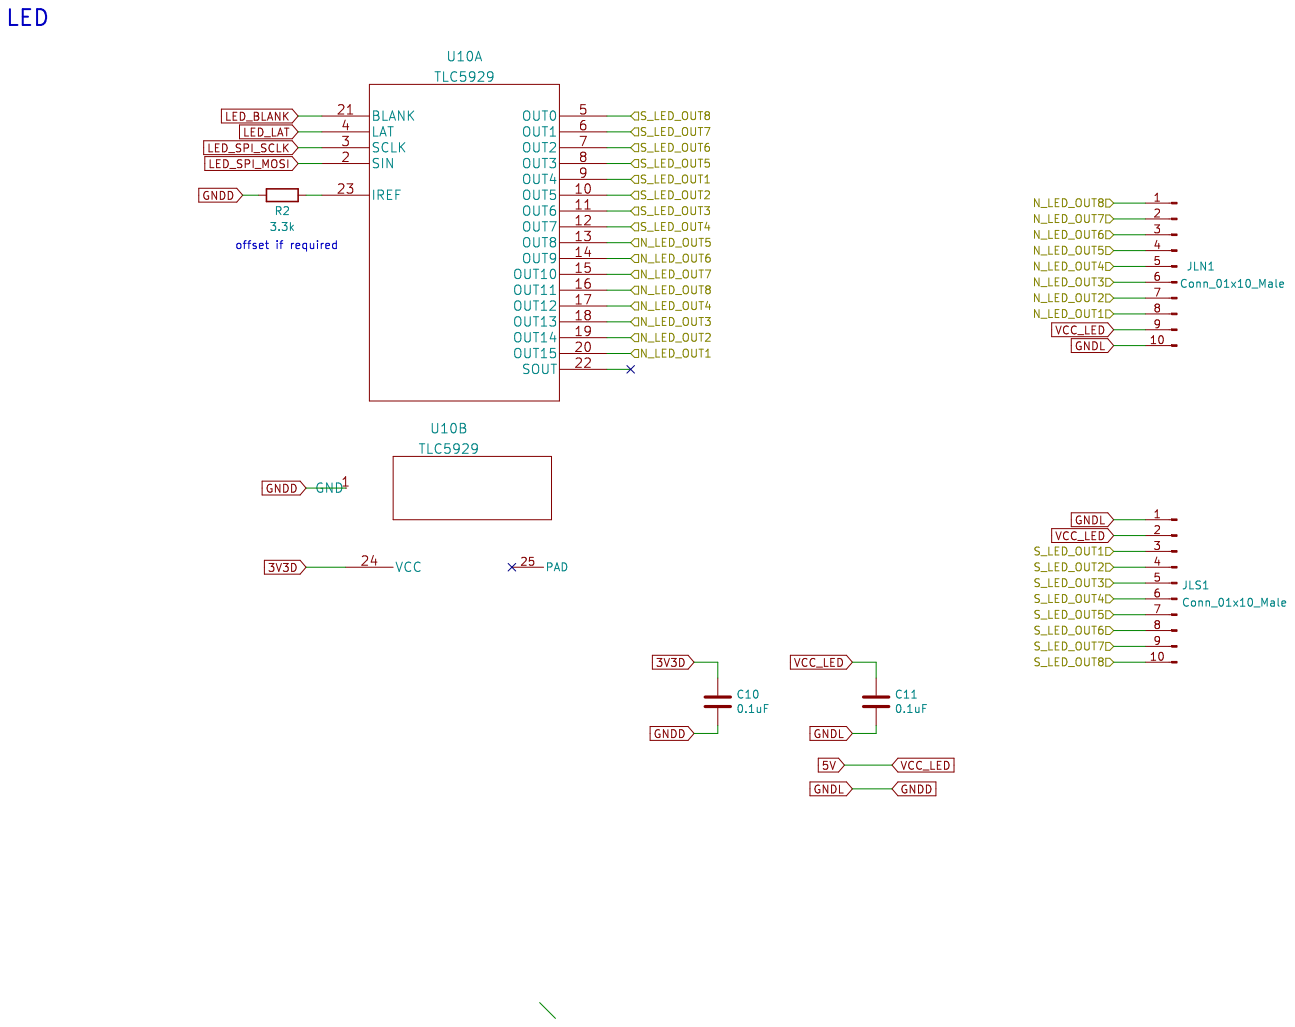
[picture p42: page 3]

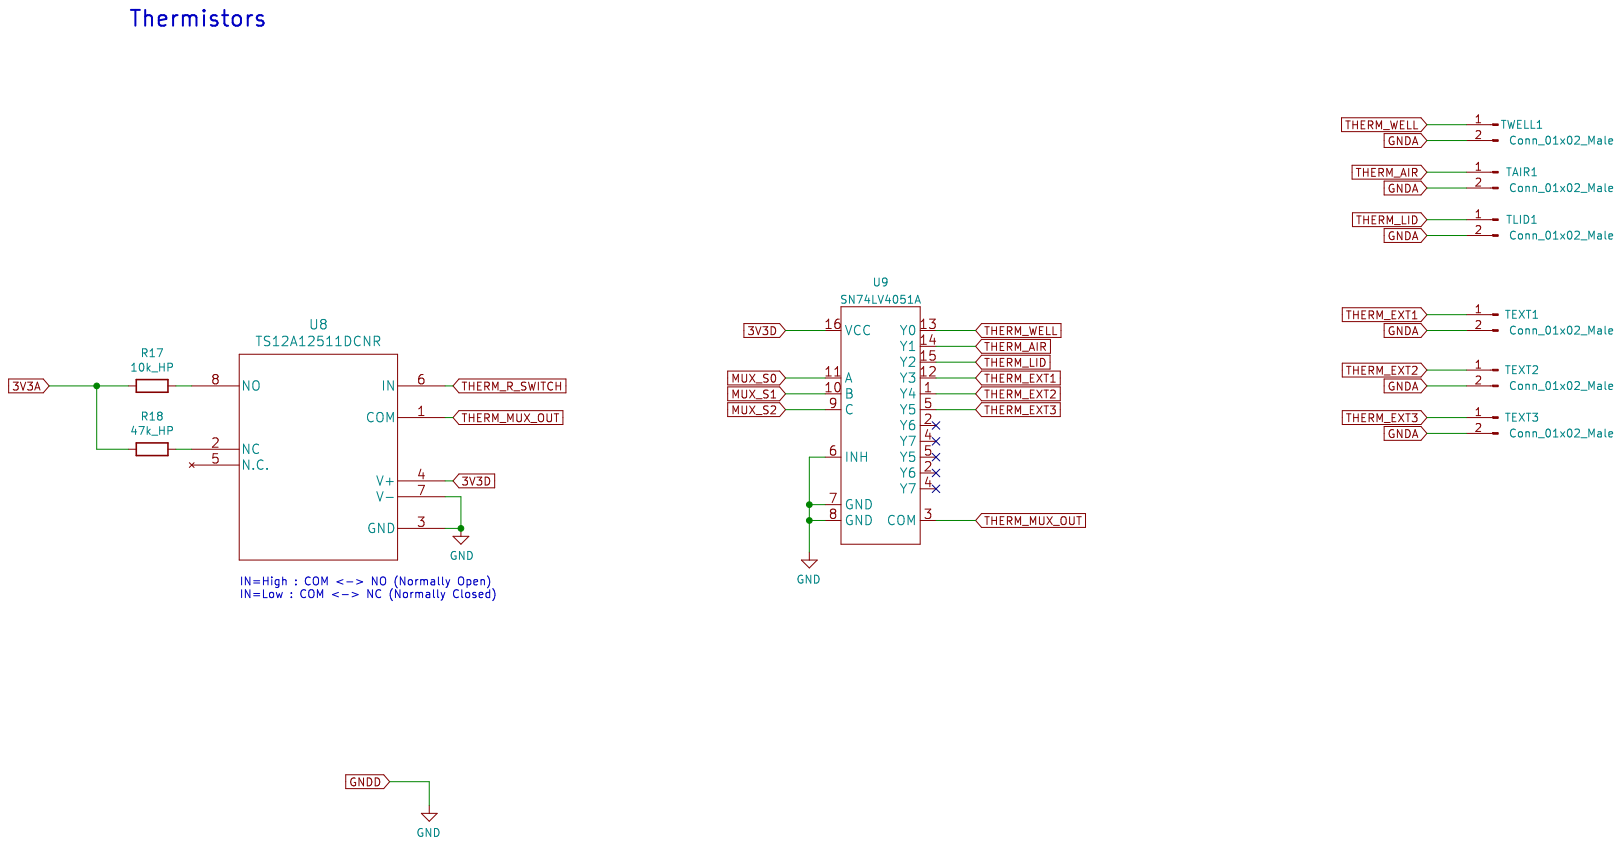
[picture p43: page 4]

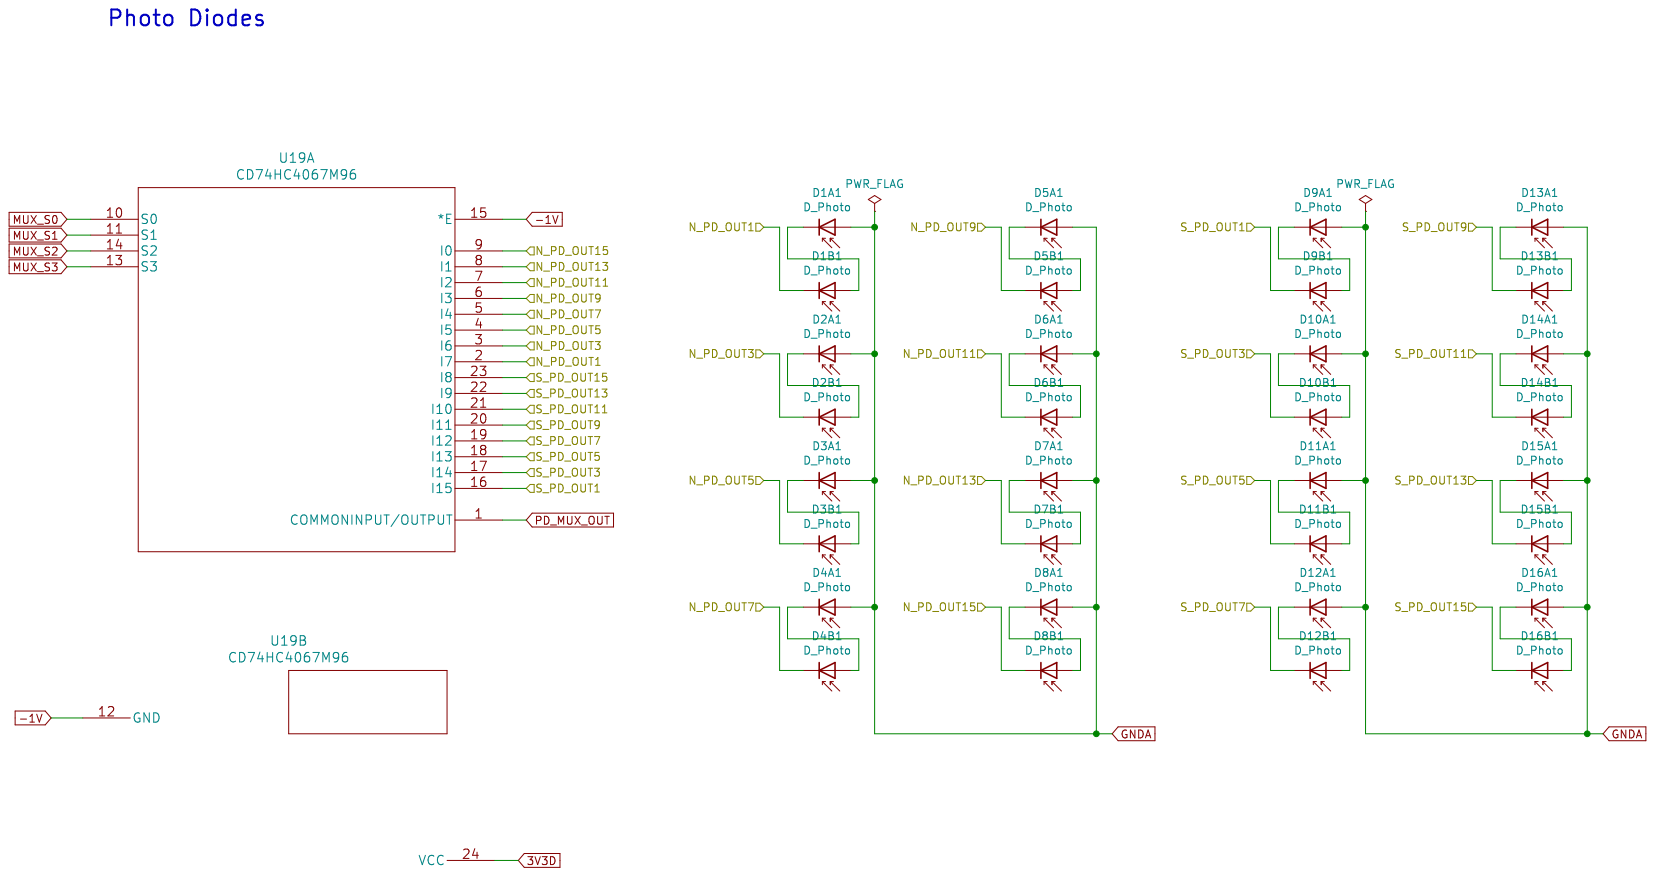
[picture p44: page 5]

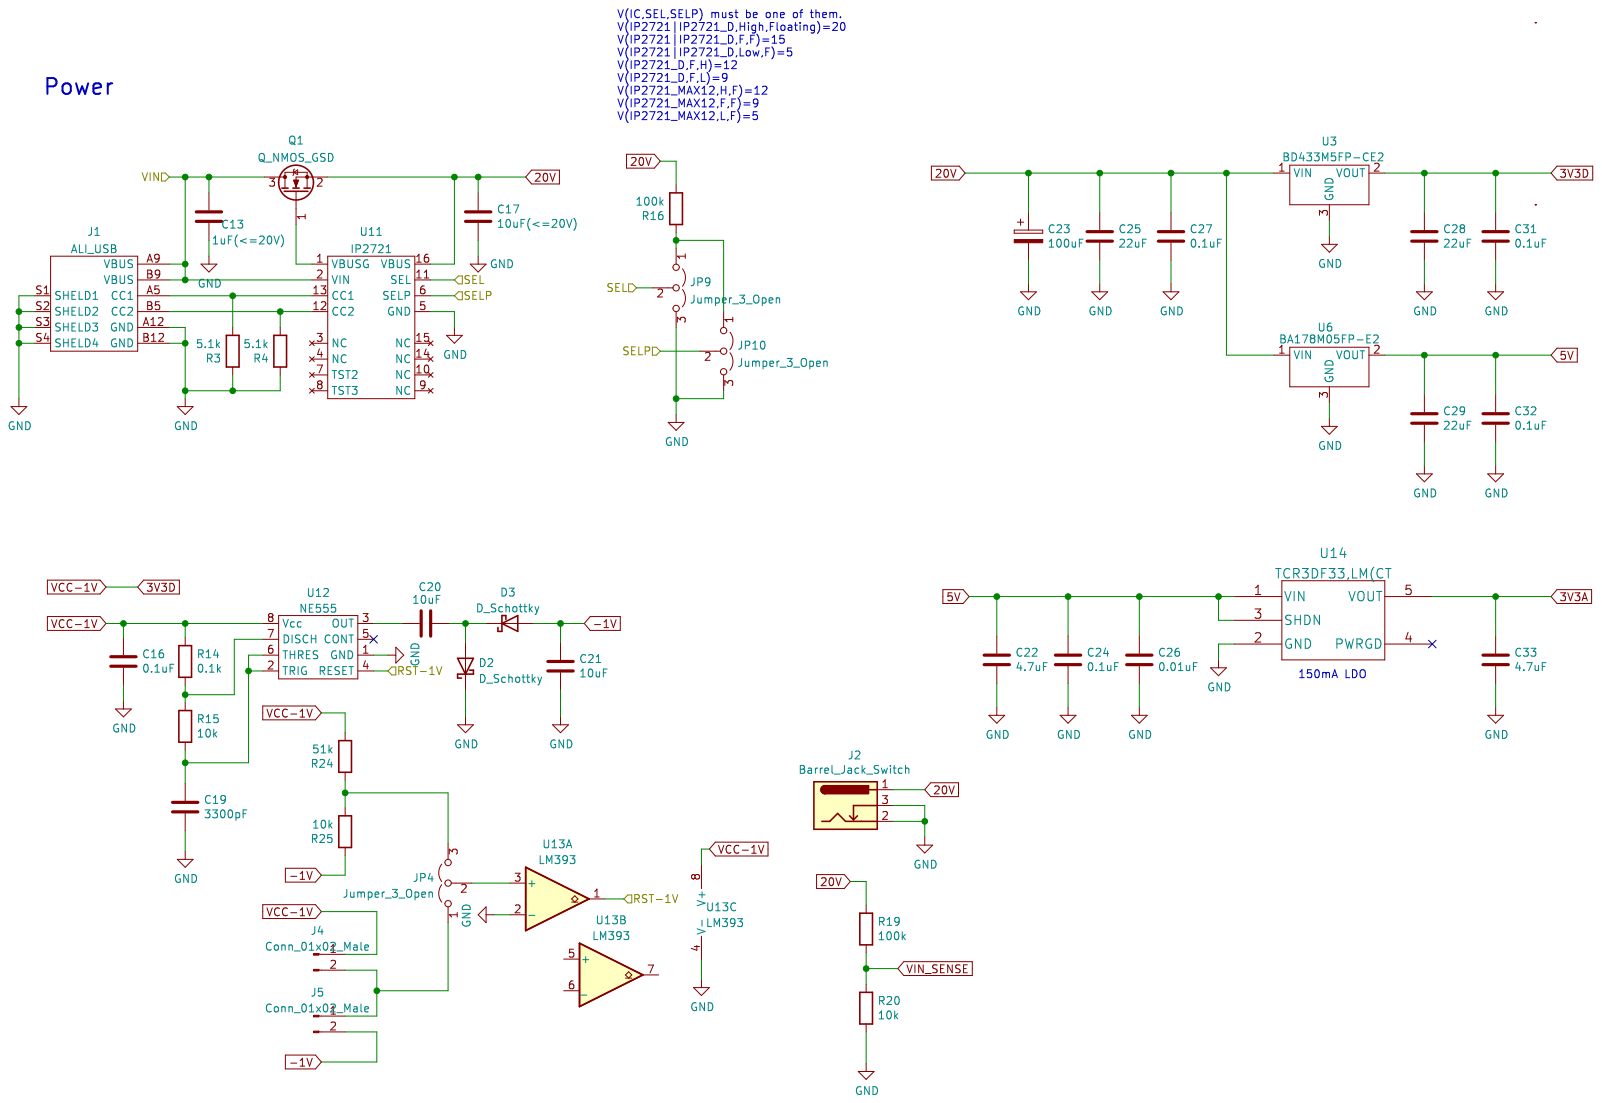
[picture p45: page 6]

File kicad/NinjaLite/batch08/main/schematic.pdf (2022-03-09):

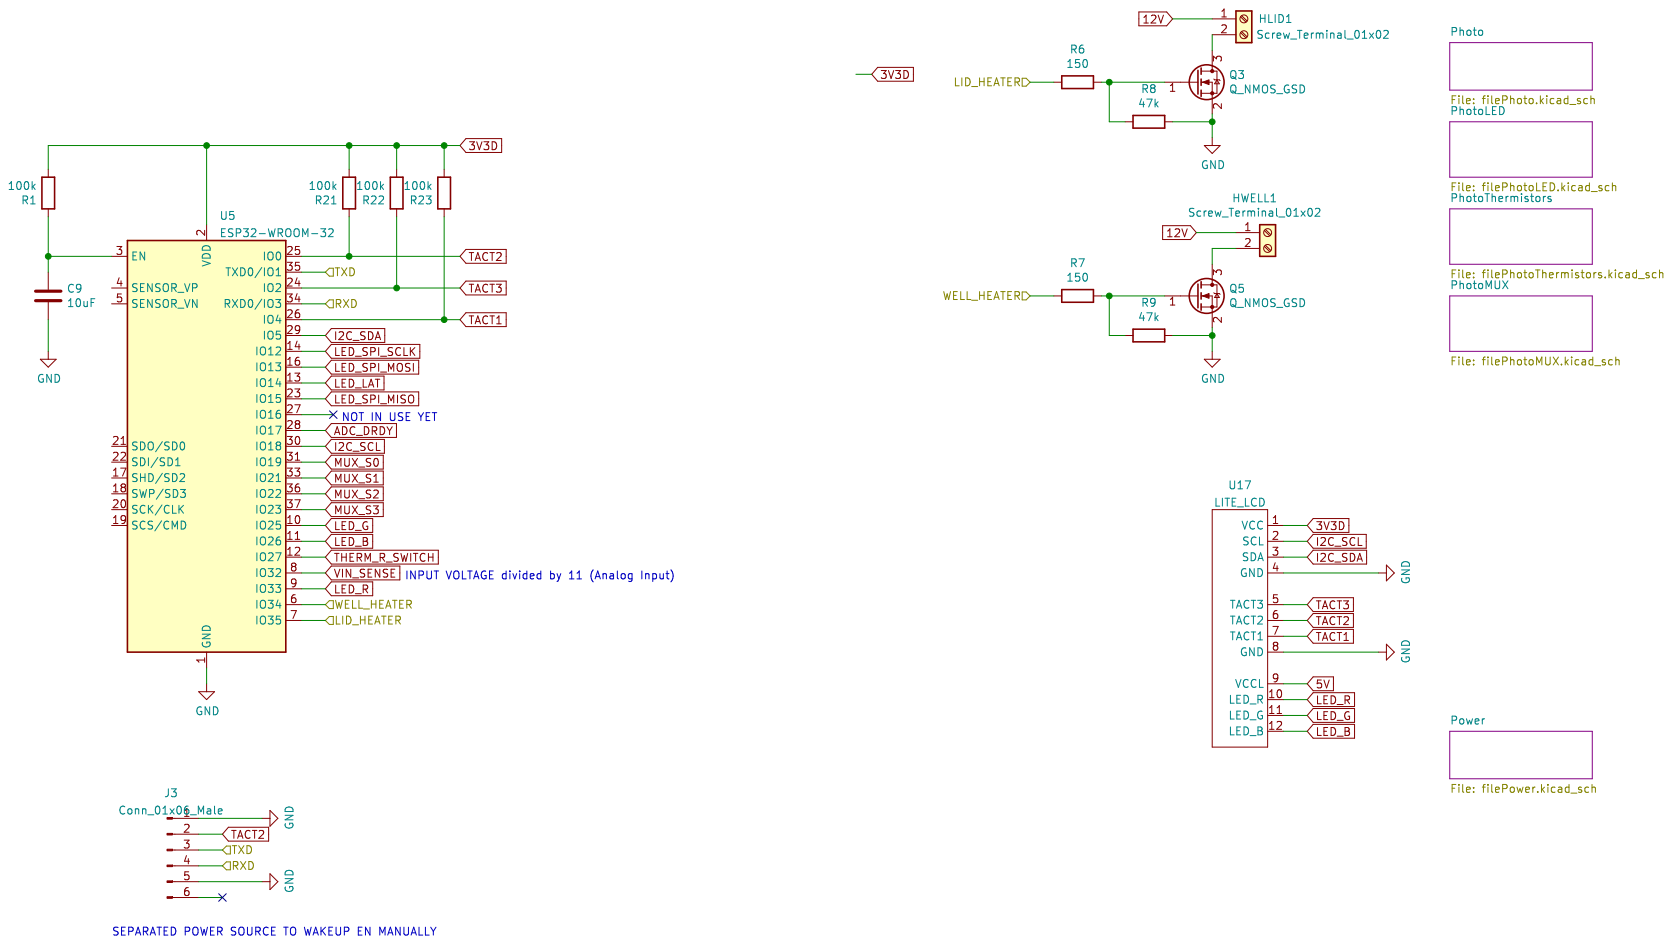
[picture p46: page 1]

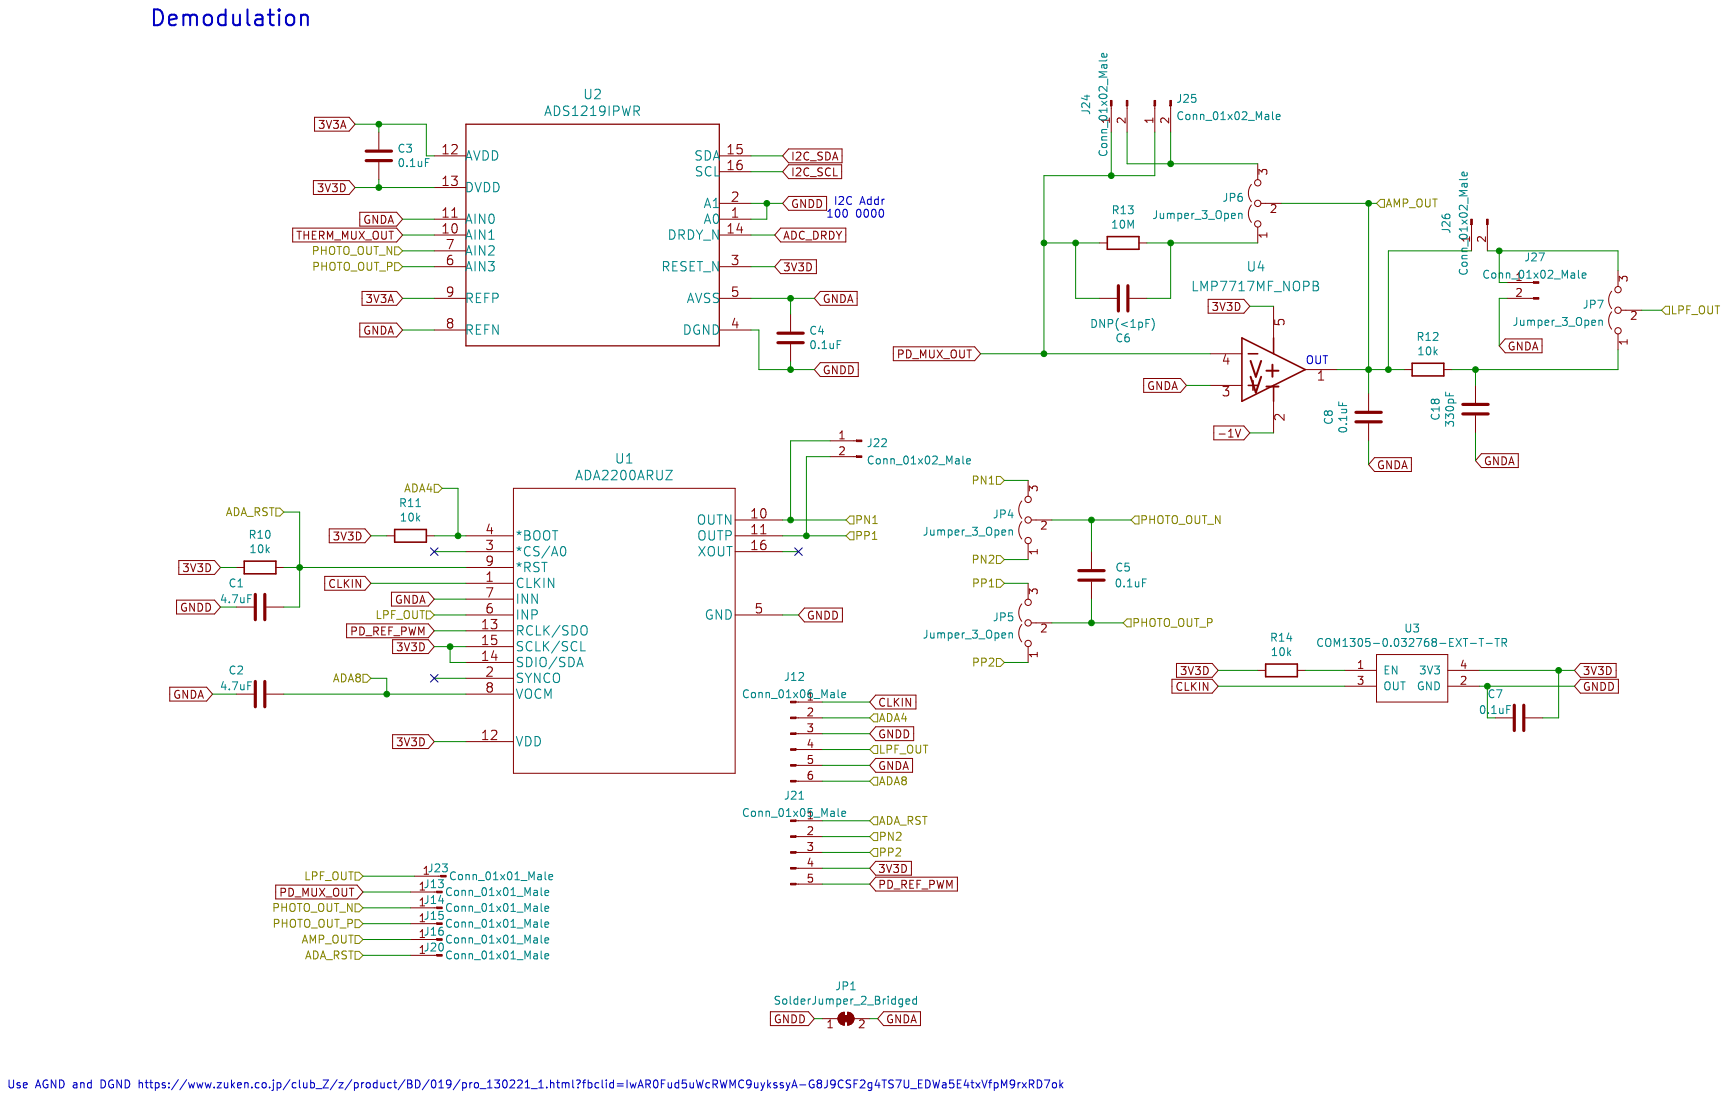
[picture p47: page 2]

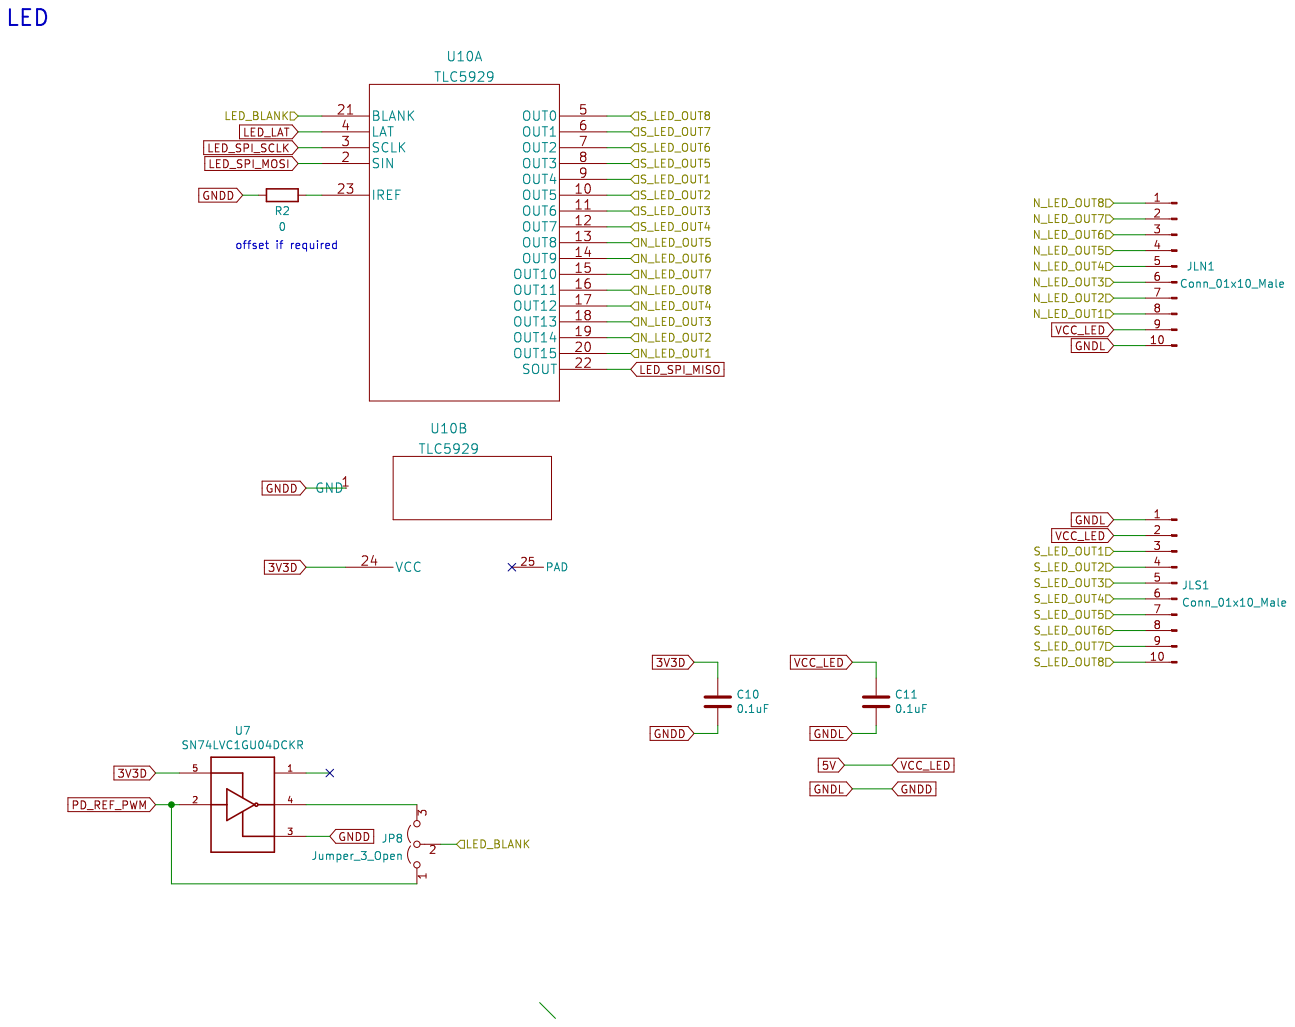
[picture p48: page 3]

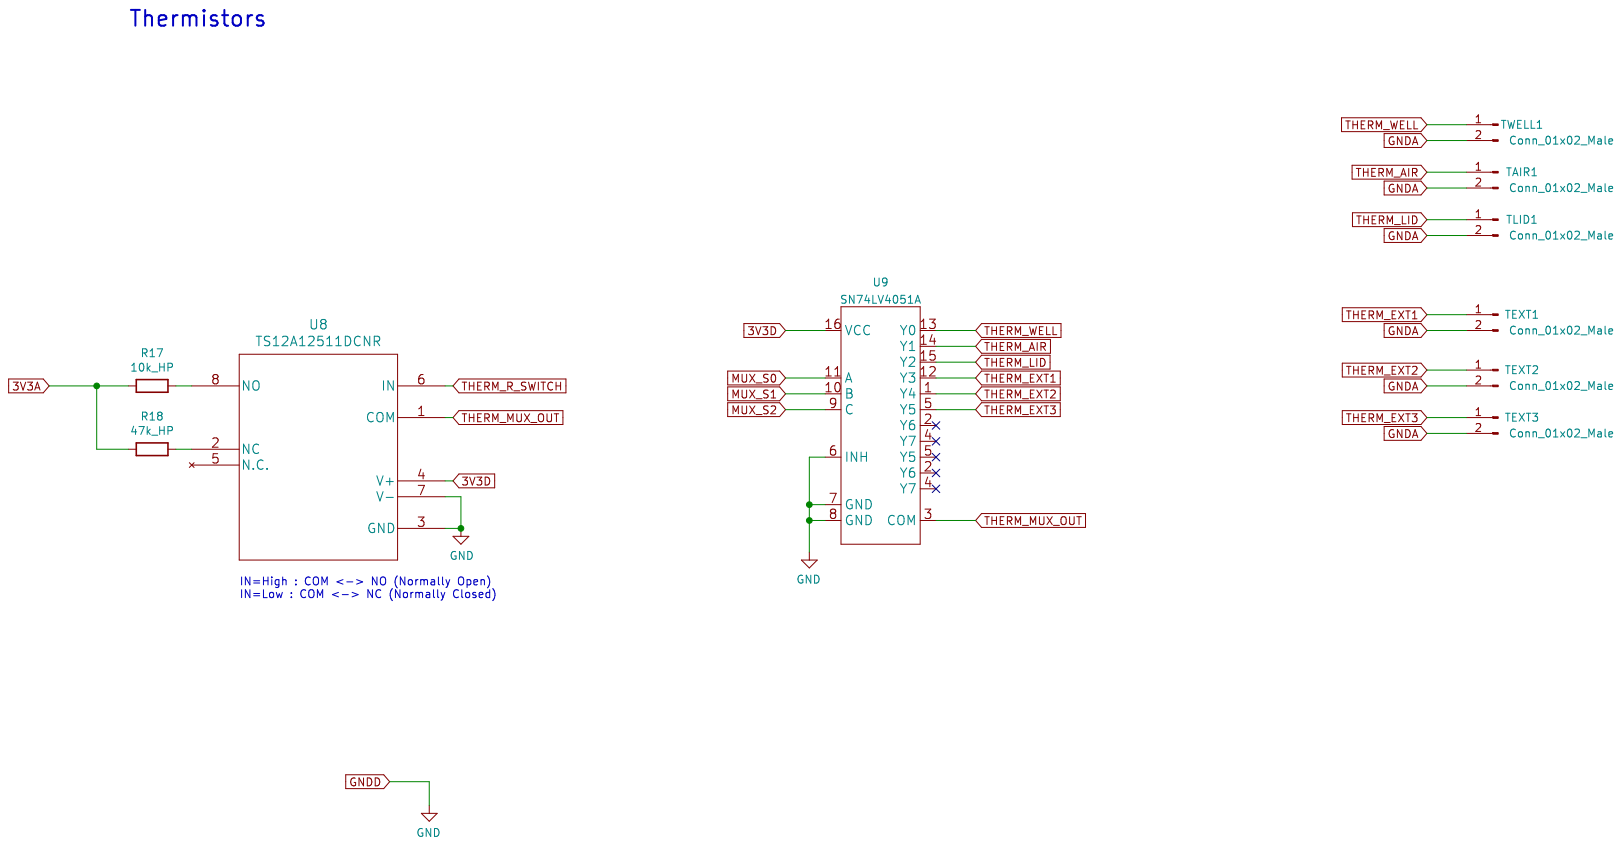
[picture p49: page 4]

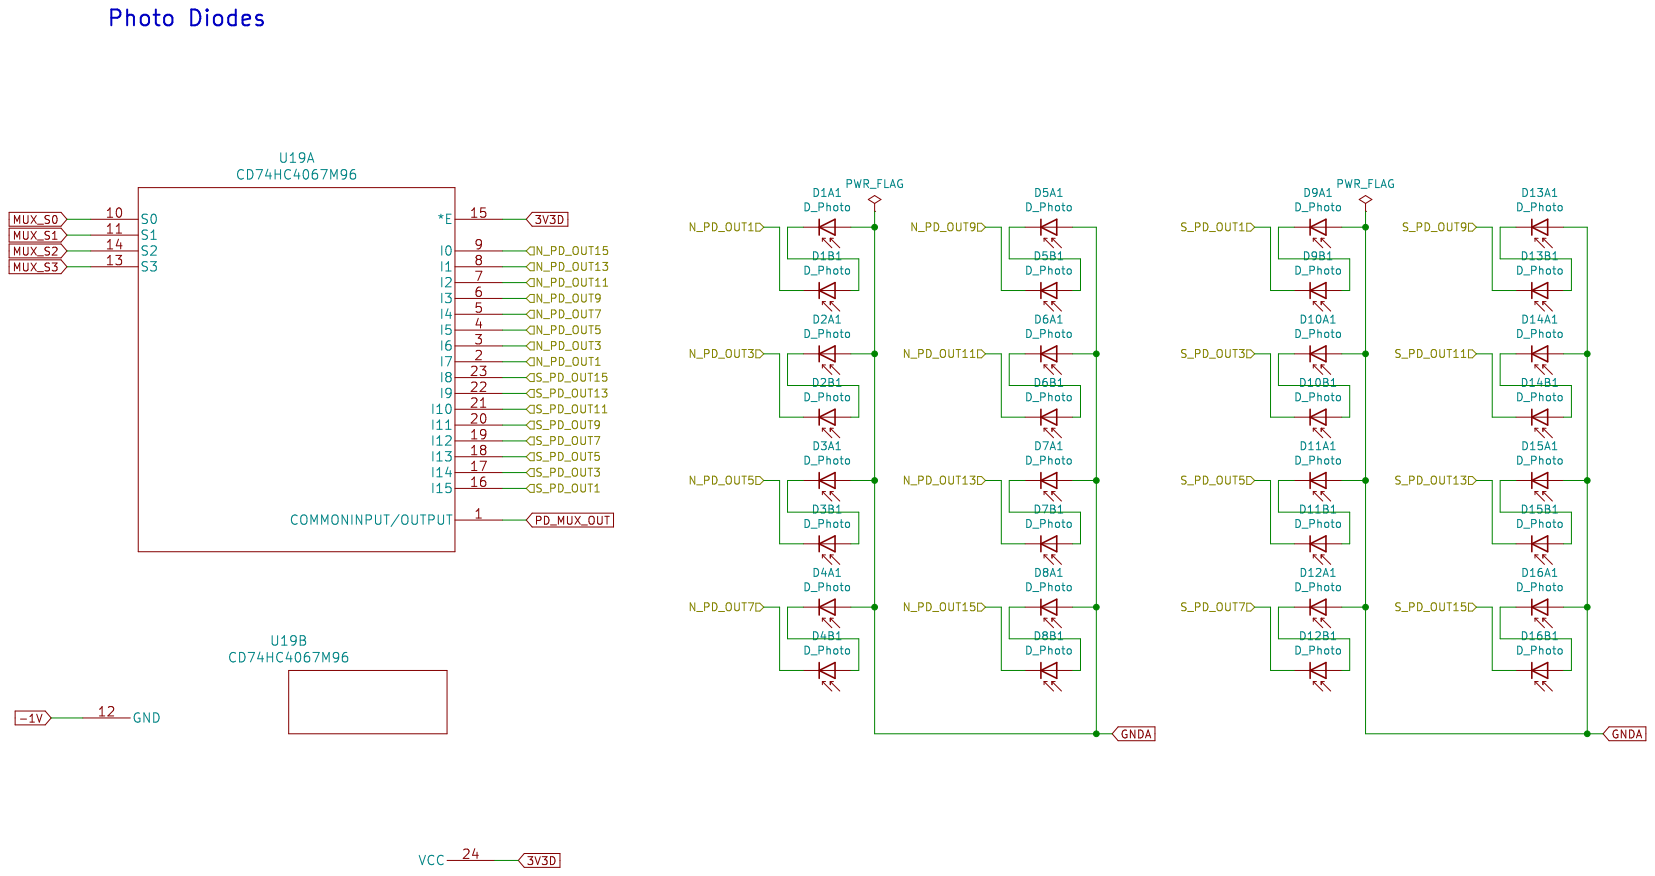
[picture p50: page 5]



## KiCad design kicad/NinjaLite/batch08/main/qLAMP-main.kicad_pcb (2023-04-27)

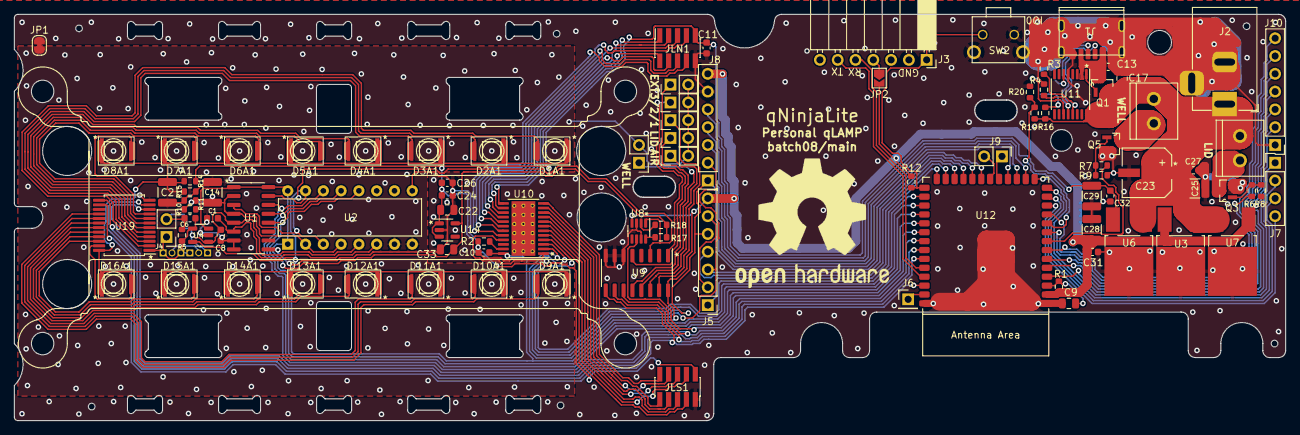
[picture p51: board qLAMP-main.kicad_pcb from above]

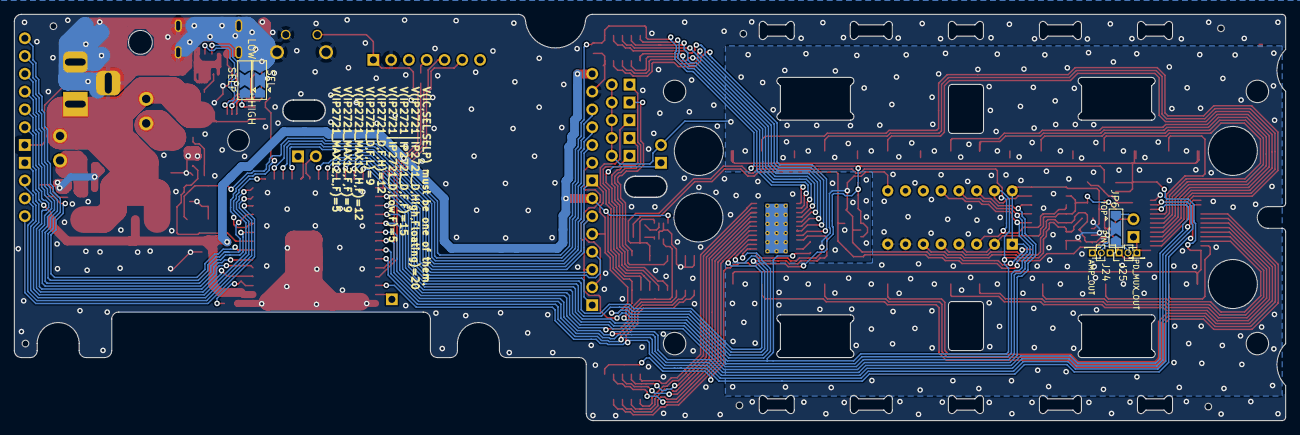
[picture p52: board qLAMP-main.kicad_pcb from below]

Board: 2 copper layers, 181.5 x 58.0 mm, 102 parts (7 on the bottom side), 104 nets.

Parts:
C1, C10, C11, C24, C27, C31, C32: 0.1uF; C_0603_1608Metric
C2, C14, C25, C28, C29: 22uF; C_1210_3225Metric
C6: 5pF; C_0603_1608Metric
C8: DNP; C_0603_1608Metric
C9: 10uF; C_0805_2012Metric
C13: 1uF(<=20V); C_0603_1608Metric
C17: 10uF(<=20V); C_0805_2012Metric
C22, C33: 4.7uF; C_0805_2012Metric
C23: 100uF; 35TZV100M6.3X8
C26: 0.01uF; C_0603_1608Metric
D1A1, D2A1, D3A1, D4A1, D5A1, D6A1, D7A1, D8A1, D9A1, D10A1, D11A1, D12A1, D13A1, D14A1, D15A1, D16A1: D_Photo; SFH2200_2201_2240
HLID1: Screw_Terminal_01x02; TB_SeeedOPL_320110028
HWELL1: Screw_Terminal_01x02; TB_SeeedOPL_320110028
J1: ALI_USB
J2: Barrel_Jack_Switch; BarrelJack_Horizontal
J3: Conn_01x07_Male; PinSocket_1x07_P2.54mm_Horizontal
J4: Conn_01x02_Male; PinHeader_1x02_P2.54mm_Vertical
J5, J8: Conn_01x07_Male; PinHeader_1x07_P2.54mm_Vertical
J6: Conn_01x01_Pin; PinHeader_1x01_P2.54mm_Vertical
J7: Conn_01x04_Male; PinHeader_1x04_P2.54mm_Vertical
J9: Conn_01x02_Pin; PinHeader_1x02_P2.54mm_Vertical
J10: Conn_01x07_Pin; PinHeader_1x07_P2.54mm_Vertical
J13, J16: Conn_01x01_Male; PinHeader_1x01_P1.27mm_Vertical
J24, J25: Conn_01x02_Male; PinHeader_1x02_P1.27mm_Vertical
JLN1: Conn_01x10_Male; PinSocket_2x05_P1.27mm_Vertical_SMD
JLS1: Conn_01x10_Male; PinSocket_2x05_P1.27mm_Vertical_SMD
JP1: SolderJumper_2_Bridged; SolderJumper-2_P1.3mm_Bridged_RoundedPad1.0x1.5mm
JP2: Jumper_2_Bridged; SolderJumper-2_P1.3mm_Open_TrianglePad1.0x1.5mm
JP6, JP9, JP10: Jumper_3_Open; SolderJumper-3_P2.0mm_Open_TrianglePad1.0x1.5mm
Q1, Q3, Q5: Q_NMOS_GSD; SOT95P240X112-3N
R1, R12, R15, R16, R19: 100k; R_0603_1608Metric
R2: 3.3k; R_0603_1608Metric
R3, R4: 5.1k; R_0603_1608Metric
R5: 10M; R_0603_1608Metric
R6, R7: 150; R_0603_1608Metric
R8, R9: 47k; R_0603_1608Metric
R10, R11, R18: 47k_HP; R_0603_1608Metric
R14, R20: 10k; R_0603_1608Metric
R17: 10k_HP; R_0603_1608Metric
SW2: TACTILE_4; SW_TH_Tactile_alps_SKHHLPA010
TAIR1: Conn_01x02_Male; PinHeader_1x02_P2.54mm_Vertical
TEXT1, TEXT2, TEXT3: Conn_01x02_Male; PinHeader_1x02_P2.54mm_Vertical
TLID1: Conn_01x02_Male; PinHeader_1x02_P2.54mm_Vertical
TWELL1: Conn_01x02_Male; PinHeader_1x02_P2.54mm_Vertical
U1: NAU7802; SOIC-16_3.9x9.9mm_P1.27mm
U2: NAU7802; DIP-16_W7.62mm
U3: BD433M5FP-CE2; REG_TO252-3
U4: LMP7717MF_NOPB; SOT-23-5
U6: BA178M05FP-E2; REG_TO252-3
U7: BD433M5FP-CE2; REG_TO252-3-INV
U8: TS12A12511DCNR; SOT-23-8-8.3mil
U9: SN74LV4051A; SOIC-16_3.9x9.9mm_P1.27mm
U10: TLC5929; HTSSOP-24-1EP_4.4x7.8mm_P0.65mm_EP3.4x7.8mm_Mask2.4x4.68mm_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
U11: IP2721; TSSOP-16_4.4x5mm_P0.65mm
U12: ESP32-­S3-­WROOM­-1; ESP32-S3-WROOM-1
U14: TCR3DF33,LM(CT; SOT-23-5
U19: CD74HC4067M96; SSOP-24_5.3x8.2mm_P0.65mm-0.83mil

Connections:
3V3A: C33.1, R10.1, R17.1, R18.1, U1.1 (REFP), U1.16 (AVDD), U2.1 (REFP), U2.16 (AVDD), U4.3 (IN+), U14.5 (VOUT)
3V3D: C10.1, C28.1, C31.1, J5.7, J8.7, J10.2, JP2.2 (B), R1.2, R12.2, U1.15 (DVDD), U2.15 (DVDD), U3.2 (VOUT), U4.5 (V+), U7.2 (VOUT), U8.4 (V+), U9.16 (VCC), U10.24 (VCC), U12.2 (3V3)
5V: C11.1, C22.1, C24.1, C26.1, C29.1, C32.1, JLN1.9, JLS1.2, R14.1, U6.2 (VOUT), U14.1 (VIN), U14.3 (SHDN)
/BOOTMODE: J3.1, R12.1, SW2.1, U12.27 (IO0)
/IO1: J6.1, U12.39 (IO1)
/IO4: J10.3, U12.4 (IO4)
/IO5: J10.4, U12.5 (IO5)
/IO6: J10.5, U12.6 (IO6)
/IO11: J9.1, U12.19 (IO11)
/IO12: J9.2, U12.20 (IO12)
/IO16: J10.6, U12.9 (IO16)
/IO18: J10.7, U12.11 (IO18)
/LCD_CS: J8.5, U12.16 (IO46)
/LCD_DC/RS: J8.3, U12.18 (IO10)
/LCD_RESET: J8.4, U12.17 (IO9)
/LID_HEATER: R6.2, U12.7 (IO7)
/MISO: J5.2, J5.6, U12.22 (IO14)
/Photo/AMP_OUT: C8.1, J16.1, JP6.2 (C), U1.5 (VIN2P), U2.5 (VIN2P), U4.1 (OUT)
/Photo/VBG: C1.1, U1.6 (VBG), U2.6 (VBG)
/PhotoLED/N_LED_OUT1: JLN1.8, U10.20 (OUT15)
/PhotoLED/N_LED_OUT2: JLN1.7, U10.19 (OUT14)
/PhotoLED/N_LED_OUT3: JLN1.6, U10.18 (OUT13)
/PhotoLED/N_LED_OUT4: JLN1.5, U10.17 (OUT12)
/PhotoLED/N_LED_OUT5: JLN1.4, U10.16 (OUT11)
/PhotoLED/N_LED_OUT6: JLN1.3, U10.15 (OUT10)
/PhotoLED/N_LED_OUT7: JLN1.2, U10.14 (OUT9)
/PhotoLED/N_LED_OUT8: JLN1.1, U10.13 (OUT8)
/PhotoLED/S_LED_OUT1: JLS1.3, U10.5 (OUT0)
/PhotoLED/S_LED_OUT2: JLS1.4, U10.6 (OUT1)
/PhotoLED/S_LED_OUT3: JLS1.5, U10.7 (OUT2)
/PhotoLED/S_LED_OUT4: JLS1.6, U10.8 (OUT3)
/PhotoLED/S_LED_OUT5: JLS1.7, U10.9 (OUT4)
/PhotoLED/S_LED_OUT6: JLS1.8, U10.10 (OUT5)
/PhotoLED/S_LED_OUT7: JLS1.9, U10.11 (OUT6)
/PhotoLED/S_LED_OUT8: JLS1.10, U10.12 (OUT7)
/PhotoMUX/N_PD_OUT1: D1A1.2 (A), U19.2 (I7)
/PhotoMUX/N_PD_OUT3: D2A1.2 (A), U19.3 (I6)
/PhotoMUX/N_PD_OUT5: D3A1.2 (A), U19.4 (I5)
/PhotoMUX/N_PD_OUT7: D4A1.2 (A), U19.5 (I4)
/PhotoMUX/N_PD_OUT9: D5A1.2 (A), U19.6 (I3)
/PhotoMUX/N_PD_OUT11: D6A1.2 (A), U19.7 (I2)
/PhotoMUX/N_PD_OUT13: D7A1.2 (A), U19.8 (I1)
/PhotoMUX/N_PD_OUT15: D8A1.2 (A), U19.9 (I0)
/PhotoMUX/S_PD_OUT1: D9A1.2 (A), U19.16 (I15)
/PhotoMUX/S_PD_OUT3: D10A1.2 (A), U19.17 (I14)
/PhotoMUX/S_PD_OUT5: D11A1.2 (A), U19.18 (I13)
/PhotoMUX/S_PD_OUT7: D12A1.2 (A), U19.19 (I12)
/PhotoMUX/S_PD_OUT9: D13A1.2 (A), U19.20 (I11)
/PhotoMUX/S_PD_OUT11: D14A1.2 (A), U19.21 (I10)
/PhotoMUX/S_PD_OUT13: D15A1.2 (A), U19.22 (I9)
/PhotoMUX/S_PD_OUT15: D16A1.2 (A), U19.23 (I8)
/Power/SEL: JP9.2 (C), U11.11 (SEL)
/Power/SELP: JP10.2 (C), U11.6 (SELP)
/Power/VIN: C13.1, J1.A9 (VBUS), J1.B9 (VBUS), Q1.3 (D), U11.2 (VIN)
/RXD: J3.5, U12.36 (IO44/RXD0)
/SD_CLK: J7.4, U12.12 (IO8)
/SD_CS: J7.1, U12.15 (IO3)
/SD_MISO: J7.3, U12.13 (IO19)
/SD_MOSI: J7.2, U12.14 (IO20)
/TP_CS: J5.4, U12.24 (IO47)
/TP_IRQ: J5.1, U12.25 (IO48)
/TXD: J3.6, U12.37 (IO43/TXD0)
/WELL_HEATER: R7.2, U12.8 (IO15)
DIVIDED: C14.1, R10.2, R11.1, U1.2 (VIN1N), U1.4 (VIN2N), U2.2 (VIN1N), U2.4 (VIN2N)
GNDA: C1.2, C2.2, C8.2, C14.2, JP1.2 (B), R11.2, R15.2, TAIR1.2, TEXT1.2, TEXT2.2, TEXT3.2, TLID1.2, TWELL1.2, U1.7 (REFN), U1.8 (AVSS), U2.7 (REFN), U2.8 (AVSS), U4.2 (V-), U19.12 (GND), U19.15 (*E)
GNDD: C9.2, C10.2, C11.2, C13.2, C17.2, C22.2, C23.2, C24.2, C25.2, C26.2, C27.2, C28.2, C29.2, C31.2, C32.2, C33.2, J1.A12 (GND), J1.B12 (GND), J1.S1 (SHELD1), J1.S2 (SHELD2), J1.S3 (SHELD3), J1.S4 (SHELD4), J2.2, J2.3, J3.2, J8.6, J10.1, JLN1.10, JLS1.1, JP1.1 (A), JP9.3 (B), JP10.3 (B), Q3.2 (S), Q5.2 (S), R2.2, R3.1, R4.1, R8.1, R9.1, R20.2, SW2.2, SW2.GND, U1.9 (DVSS), U2.9 (DVSS), U3.3 (GND), U6.3 (GND), U7.3 (GND), U8.3 (GND), U8.7 (V-), U9.6 (INH), U9.7 (GND), U9.8 (GND), U10.1 (GND), U11.5 (GND), U12.1 (GND), U12.40 (GND), U12.41 (GND), U14.2 (GND)
I2C_SCL: U1.13 (SCLK), U2.13 (SCLK), U12.30 (IO37)
I2C_SDA: U1.14 (SDIO), U2.14 (SDIO), U12.31 (IO38)
LED_BLANK: U10.21 (BLANK), U12.28 (IO35)
LED_LAT: U10.4 (LAT), U12.26 (IO45)
MOSI: J5.3, J8.2, U10.2 (SIN), U12.23 (IO21)
MUX_S0: U9.11 (A), U12.33 (IO40), U19.10 (S0)
MUX_S1: U9.10 (B), U12.35 (IO42), U19.11 (S1)
MUX_S2: U9.9 (C), U12.38 (IO2), U19.14 (S2)
MUX_S3: U12.34 (IO41), U19.13 (S3)
NAU_DRDY: U1.12 (DRDY), U2.12 (DRDY), U12.29 (IO36)
unnamed: HLID1.2, Q3.3 (D)
unnamed: HWELL1.2, Q5.3 (D)
unnamed: J1.A5 (CC1), R3.2, U11.13 (CC1)
unnamed: J1.B5 (CC2), R4.2, U11.12 (CC2)
unnamed: J3.4, JP2.1 (A)
unnamed: C6.1, J4.2, JP6.1 (A), R5.2
unnamed: J24.2, J25.2, JP6.3 (B)
unnamed: JP9.1 (A), JP10.1 (A), R16.1
unnamed: Q1.1 (G), U11.1 (VBUSG)
unnamed: Q3.1 (G), R6.1, R8.2
unnamed: Q5.1 (G), R7.1, R9.2
unnamed: R18.2, U8.2 (NC)
unnamed: R17.2, U8.8 (NO)
unnamed: R2.1, U10.23 (IREF)
unnamed: C9.1, R1.1, U12.3 (EN)
PD_MUX_OUT: C6.2, J4.1, J13.1, J24.1, J25.1, R5.1, U4.4 (IN-), U19.1 (COMMONINPUT/OUTPUT)
SCLK: J5.5, J8.1, U10.3 (SCLK), U12.21 (IO13)
THERM_AIR: TAIR1.1, U9.14 (Y1)
THERM_EXT1: TEXT1.1, U9.15 (Y2)
THERM_EXT2: TEXT2.1, U9.1 (Y4)
THERM_EXT3: TEXT3.1, U9.5 (Y5)
THERM_LID: TLID1.1, U9.12 (Y3)
THERM_MUX_OUT: U1.3 (VIN1P), U2.3 (VIN1P), U8.1 (COM), U9.3 (COM)
THERM_R_SWITCH: U8.6 (IN), U12.32 (IO39)
THERM_WELL: TWELL1.1, U9.13 (Y0)
VCC: C17.1, C23.1, C25.1, C27.1, HLID1.1, HWELL1.1, J2.1, Q1.2 (S), R16.2, R19.1, U3.1 (VIN), U6.1 (VIN), U7.1 (VIN), U11.16 (VBUS)
VIN_SENSE: R19.2, R20.1, U12.10 (IO17)
VOPT: C2.1, D1A1.1 (K), D2A1.1 (K), D3A1.1 (K), D4A1.1 (K), D5A1.1 (K), D6A1.1 (K), D7A1.1 (K), D8A1.1 (K), D9A1.1 (K), D10A1.1 (K), D11A1.1 (K), D12A1.1 (K), D13A1.1 (K), D14A1.1 (K), D15A1.1 (K), D16A1.1 (K), R14.2, R15.1, U19.24 (VCC)

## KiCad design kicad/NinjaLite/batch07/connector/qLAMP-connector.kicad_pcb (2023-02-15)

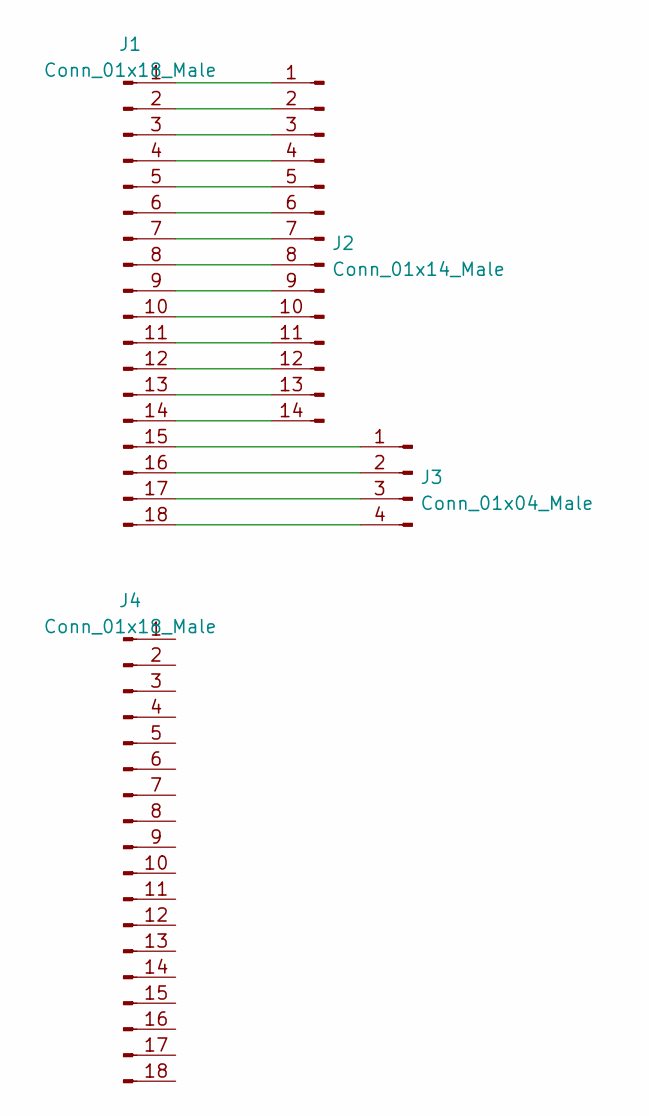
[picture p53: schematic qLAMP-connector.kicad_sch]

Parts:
J1: Conn_01x18_Male; PinSocket_2x09_P2.54mm_Vertical
J2: Conn_01x14_Male; PinSocket_1x14_P2.54mm_Vertical
J3: Conn_01x04_Male; PinSocket_1x04_P2.54mm_Vertical
J4: Conn_01x18_Male; PinSocket_2x09_P1.27mm_Vertical

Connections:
unnamed: J1.1, J2.1
unnamed: J1.2, J2.2
unnamed: J1.3, J2.3
unnamed: J1.4, J2.4
unnamed: J1.5, J2.5
unnamed: J1.6, J2.6
unnamed: J1.7, J2.7
unnamed: J1.8, J2.8
unnamed: J1.9, J2.9
unnamed: J1.10, J2.10
unnamed: J1.11, J2.11
unnamed: J1.12, J2.12
unnamed: J1.13, J2.13
unnamed: J1.14, J2.14
unnamed: J1.15, J3.1
unnamed: J1.16, J3.2
unnamed: J1.17, J3.3
unnamed: J1.18, J3.4

Board: 2 copper layers, 4 parts (0 on the bottom side), 18 nets, no tracks yet.

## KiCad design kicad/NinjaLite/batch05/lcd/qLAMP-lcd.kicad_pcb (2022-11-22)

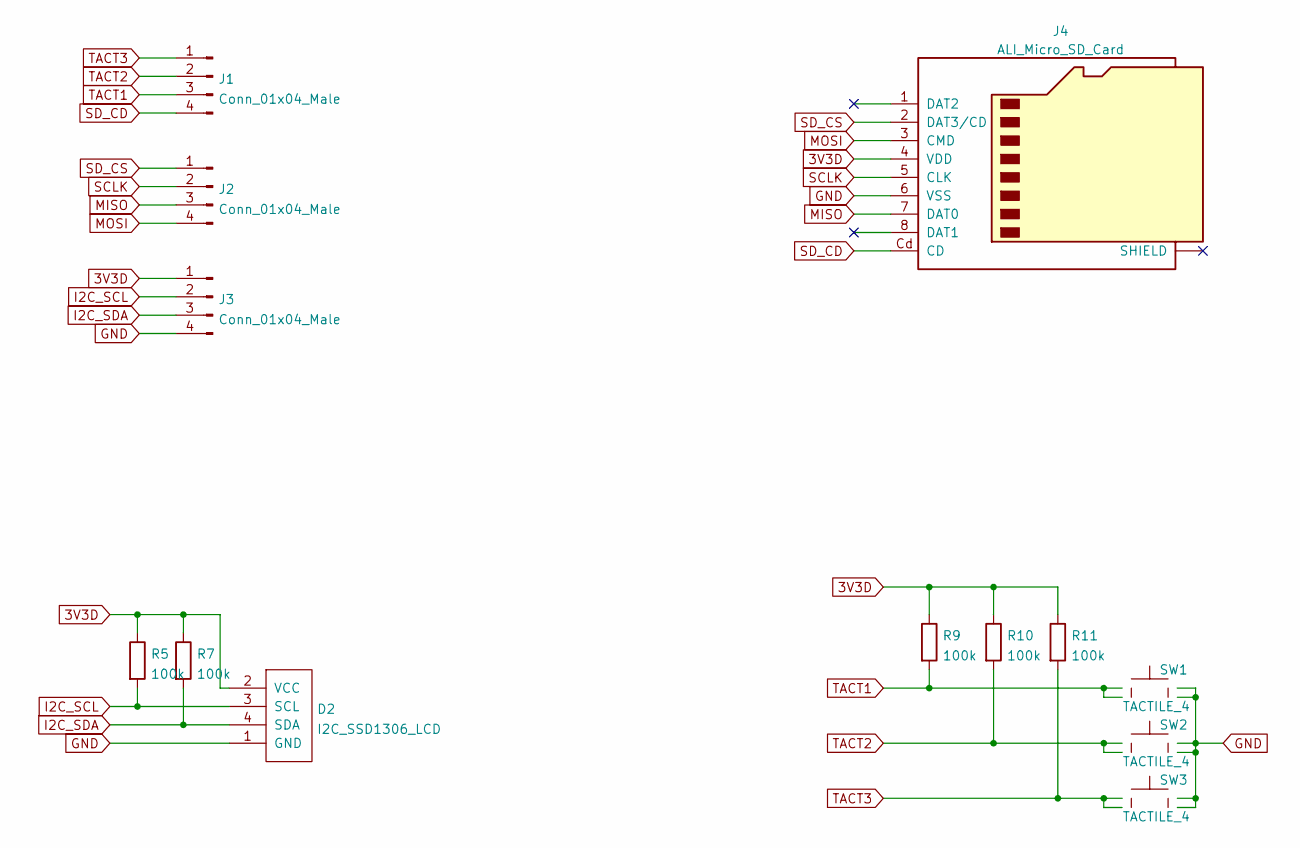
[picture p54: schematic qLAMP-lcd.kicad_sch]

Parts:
D2: I2C_SSD1306_LCD; ALI_I2C_LCD
J1, J2, J3: Conn_01x04_Male; PinHeader_1x04_P2.54mm_Vertical
J4: ALI_Micro_SD_Card; ALI_microSD
R5, R7, R9, R10, R11: 100k; R_0603_1608Metric
SW1, SW2, SW3: TACTILE_4; SW_TH_Tactile_Omron_B3F-10xx

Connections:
3V3D: D2.2 (VCC), J3.1, J4.4 (VDD), R5.1, R7.1, R9.1, R10.1, R11.1
GND: D2.1 (GND), J3.4, J4.6 (VSS), SW1.3, SW1.4, SW2.3, SW2.4, SW3.3, SW3.4
I2C_SCL: D2.3 (SCL), J3.2, R5.2
I2C_SDA: D2.4 (SDA), J3.3, R7.2
MISO: J2.3, J4.7 (DAT0)
MOSI: J2.4, J4.3 (CMD)
SCLK: J2.2, J4.5 (CLK)
SD_CD: J1.4, J4.Cd (CD)
SD_CS: J2.1, J4.2 (DAT3/CD)
TACT1: J1.3, R9.2, SW1.1, SW1.2
TACT2: J1.2, R10.2, SW2.1, SW2.2
TACT3: J1.1, R11.2, SW3.1, SW3.2

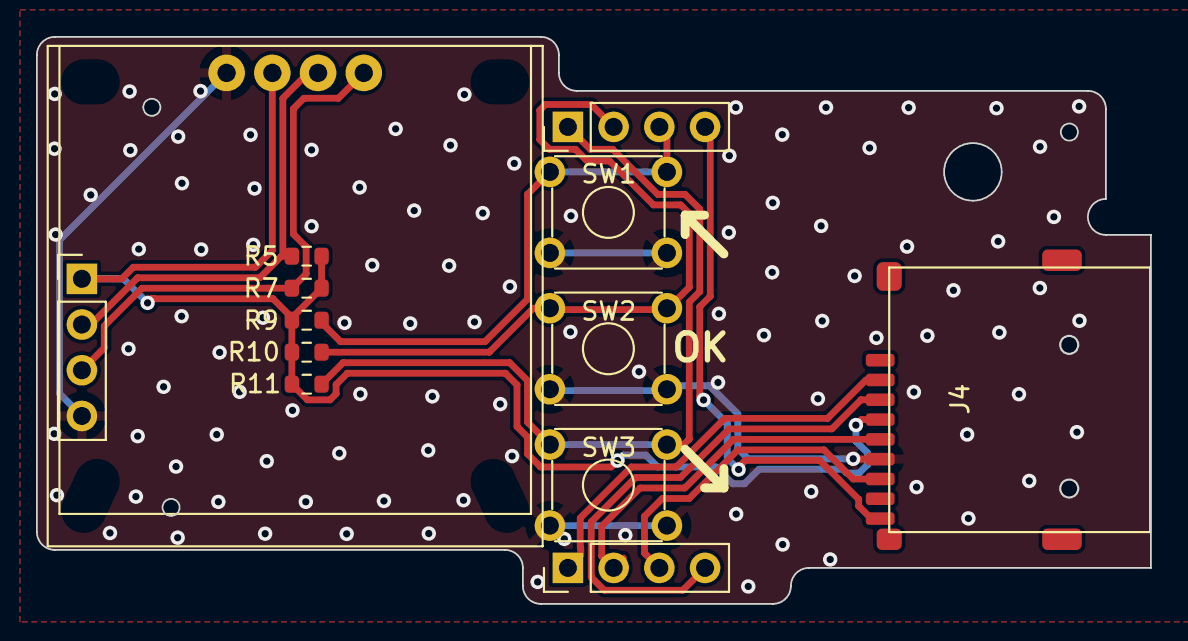
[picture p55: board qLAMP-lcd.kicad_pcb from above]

Board: 2 copper layers, 61.9 x 31.5 mm, 13 parts (0 on the bottom side), 12 nets.

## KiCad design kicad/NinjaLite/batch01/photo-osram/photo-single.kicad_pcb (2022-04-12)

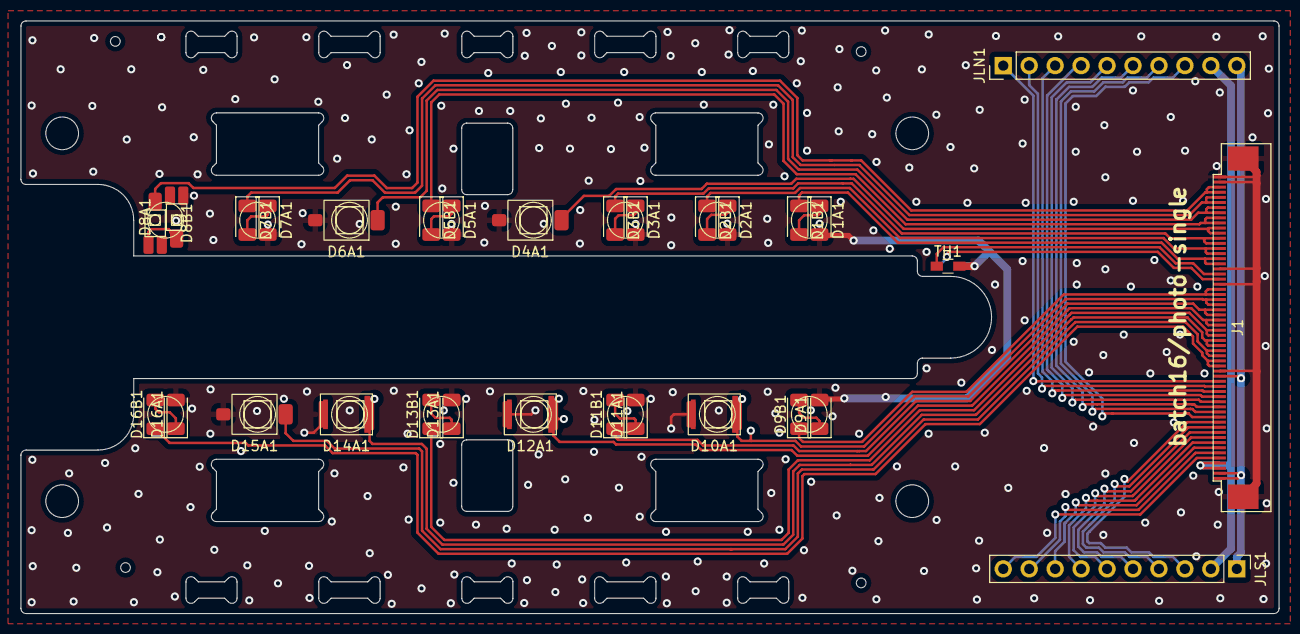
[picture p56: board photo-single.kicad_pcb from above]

Board: 2 copper layers, 123.1 x 58.0 mm, 31 parts (1 on the bottom side), 47 nets.

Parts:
D1A1, D1B1, D2A1, D2B1, D3A1, D3B1, D5A1, D5B1, D7A1, D7B1, D9A1, D9B1, D11A1, D11B1, D13A1, D13B1, D16A1, D16B1: D_Photo; D_1206_3216Metric
D4A1, D6A1, D15A1: D_Photo; SFH2440_2430_BPW34S
D8A1, D8B1: D_Photo; SFH2400
D10A1, D12A1, D14A1: D_Photo; SFH2200_2201_2240
J1: Conn_01x60_Male; FFC_60_Ali_HUISHUNFA
JLN1: Conn_01x10_Male; Pin_Header_Straight_1x10_Pitch2.54mm
JLS1: Conn_01x10_Male; Pin_Header_Straight_1x10_Pitch2.54mm
TH1, TH2: Thermistor; R_0603_HandSoldering

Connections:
/N_LED_OUT9: J1.13, JLN1.8
/N_LED_OUT10: J1.14, JLN1.7
/N_LED_OUT11: J1.15, JLN1.6
/N_LED_OUT12: J1.16, JLN1.5
/N_LED_OUT13: J1.17, JLN1.4
/N_LED_OUT14: J1.18, JLN1.3
/N_LED_OUT15: J1.19, JLN1.2
/N_LED_OUT16: J1.20, JLN1.1
/N_PD_OUT1: D1B1.1 (K), J1.43, J1.44
/N_PD_OUT3: D2B1.1 (K), J1.45, J1.46
/N_PD_OUT5: D3B1.1 (K), J1.47, J1.48
/N_PD_OUT7: D4A1.1 (K), J1.49, J1.50
/N_PD_OUT9: D5B1.1 (K), J1.51, J1.52
/N_PD_OUT11: D6A1.1 (K), J1.53, J1.54
/N_PD_OUT13: D7B1.1 (K), J1.55, J1.56
/N_PD_OUT15: D8B1.1 (K), J1.57, J1.58
/S_LED_OUT1: J1.12, JLS1.3
/S_LED_OUT2: J1.11, JLS1.4
/S_LED_OUT3: J1.10, JLS1.5
/S_LED_OUT4: J1.9, JLS1.6
/S_LED_OUT5: J1.8, JLS1.7
/S_LED_OUT6: J1.7, JLS1.8
/S_LED_OUT7: J1.6, JLS1.9
/S_LED_OUT8: J1.5, JLS1.10
/S_PD_OUT1: D9B1.1 (K), J1.37, J1.38
/S_PD_OUT3: D10A1.1 (K), J1.35, J1.36
/S_PD_OUT5: D11B1.1 (K), J1.33, J1.34
/S_PD_OUT7: D12A1.1 (K), J1.31, J1.32
/S_PD_OUT9: D13B1.1 (K), J1.29, J1.30
/S_PD_OUT11: D14A1.1 (K), J1.27, J1.28
/S_PD_OUT13: D15A1.1 (K), J1.25, J1.26
/S_PD_OUT15: D16B1.1 (K), J1.23, J1.24
GNDA: D1A1.2 (A), D2A1.2 (A), D3A1.2 (A), D4A1.2 (A), D5A1.2 (A), D6A1.2 (A), D7A1.2 (A), D8A1.2 (A), D9A1.2 (A), D10A1.2 (A), D11A1.2 (A), D12A1.2 (A), D13A1.2 (A), D14A1.2 (A), D15A1.2 (A), D16A1.2 (A), J1.22, J1.39, J1.42, J1.59, J1.60, J1.G1, J1.G2, TH1.2, TH2.2
GNDL: J1.1, J1.2, J1.21, JLN1.10, JLS1.1
unnamed: D1A1.1 (K), D1B1.2 (A)
unnamed: D2A1.1 (K), D2B1.2 (A)
unnamed: D3A1.1 (K), D3B1.2 (A)
unnamed: D5A1.1 (K), D5B1.2 (A)
unnamed: D7A1.1 (K), D7B1.2 (A)
unnamed: D8A1.1 (K), D8B1.2 (A)
unnamed: D9A1.1 (K), D9B1.2 (A)
unnamed: D11A1.1 (K), D11B1.2 (A)
unnamed: D13A1.1 (K), D13B1.2 (A)
unnamed: D16A1.1 (K), D16B1.2 (A)
unnamed: J1.40, TH2.1
unnamed: J1.41, TH1.1
VCCL: J1.3, J1.4, JLN1.9, JLS1.2

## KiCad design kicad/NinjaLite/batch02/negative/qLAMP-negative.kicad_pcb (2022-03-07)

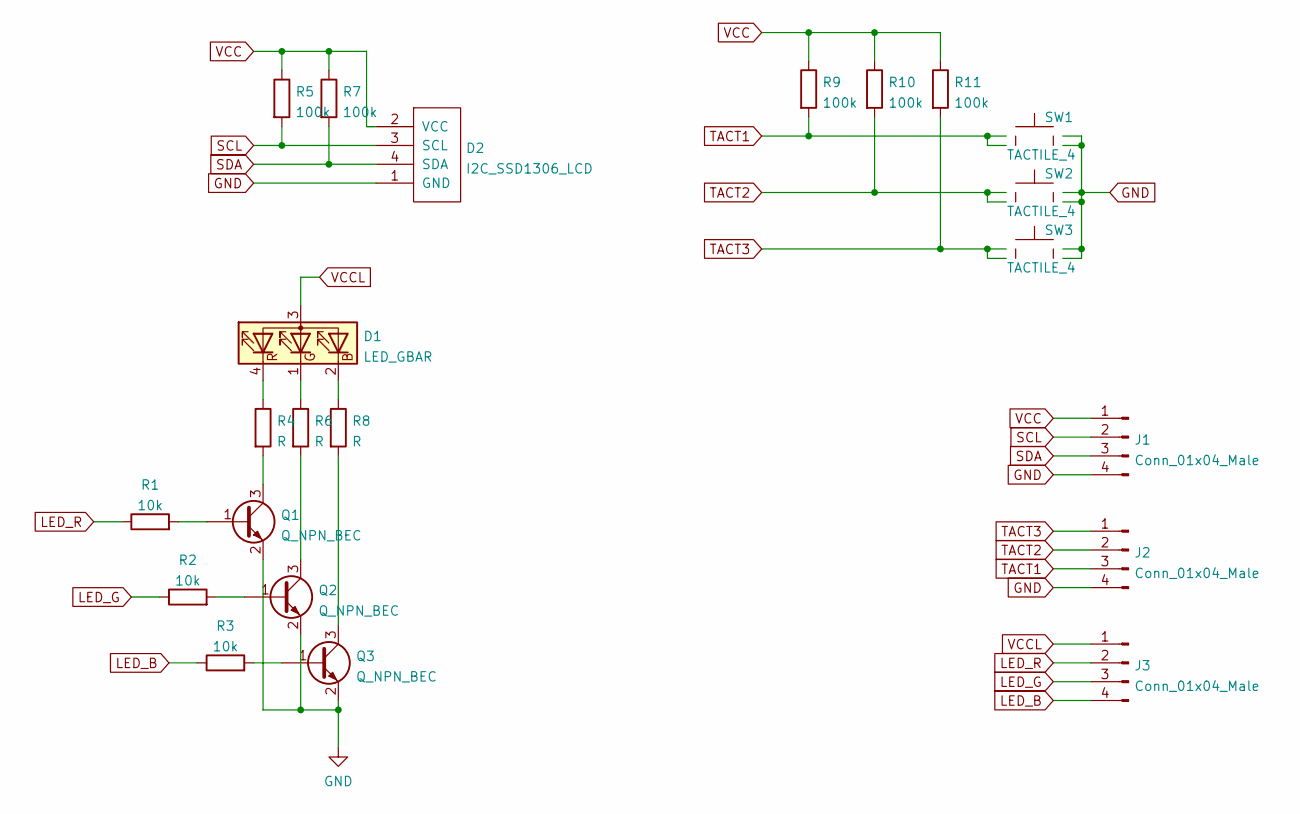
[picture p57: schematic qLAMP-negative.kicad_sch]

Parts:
D1: LED_GBAR; LED_D5.0mm-4_RGB
D2: I2C_SSD1306_LCD
J1, J2, J3: Conn_01x04_Male; PinHeader_1x04_P2.54mm_Vertical
Q1, Q2, Q3: Q_NPN_BEC; SOT-23
R1, R2, R3: 10k; R_0603_1608Metric
R4, R6, R8: R; R_0603_1608Metric
R5, R7, R9, R10, R11: 100k; R_0603_1608Metric
SW1, SW2, SW3: TACTILE_4; SW_TH_Tactile_Omron_B3F-10xx

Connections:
GND: D2.1 (GND), J1.4, J2.4, Q1.2 (E), Q2.2 (E), Q3.2 (E), SW1.3, SW1.4, SW2.3, SW2.4, SW3.3, SW3.4
LED_B: J3.4, R3.1
LED_G: J3.3, R2.1
LED_R: J3.2, R1.1
unnamed: D1.1 (GK), R6.1
unnamed: D1.2 (BK), R8.1
unnamed: D1.4 (RK), R4.1
unnamed: Q1.1 (B), R1.2
unnamed: Q1.3 (C), R4.2
unnamed: Q2.1 (B), R2.2
unnamed: Q2.3 (C), R6.2
unnamed: Q3.1 (B), R3.2
unnamed: Q3.3 (C), R8.2
SCL: D2.3 (SCL), J1.2, R5.2
SDA: D2.4 (SDA), J1.3, R7.2
TACT1: J2.3, R9.2, SW1.1, SW1.2
TACT2: J2.2, R10.2, SW2.1, SW2.2
TACT3: J2.1, R11.2, SW3.1, SW3.2
VCC: D2.2 (VCC), J1.1, R5.1, R7.1, R9.1, R10.1, R11.1
VCCL: D1.3 (A), J3.1

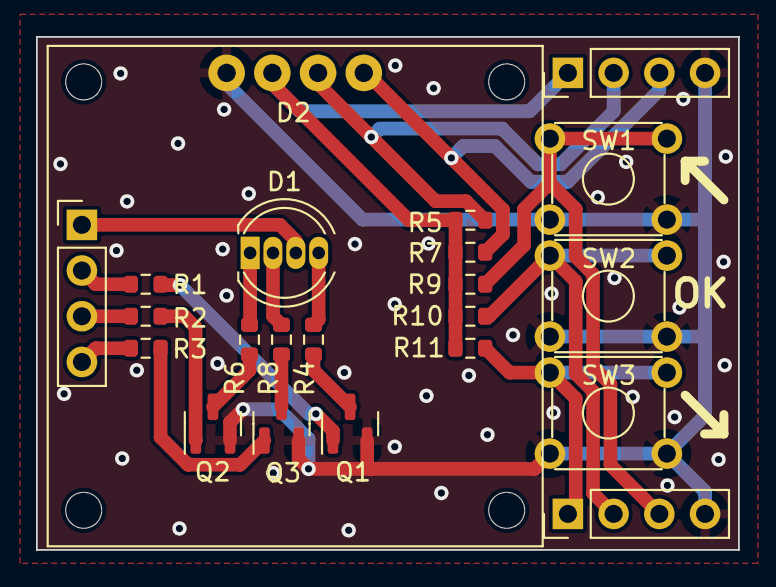
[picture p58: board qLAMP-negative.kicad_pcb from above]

Board: 2 copper layers, 39.0 x 28.5 mm, 22 parts (0 on the bottom side), 20 nets.

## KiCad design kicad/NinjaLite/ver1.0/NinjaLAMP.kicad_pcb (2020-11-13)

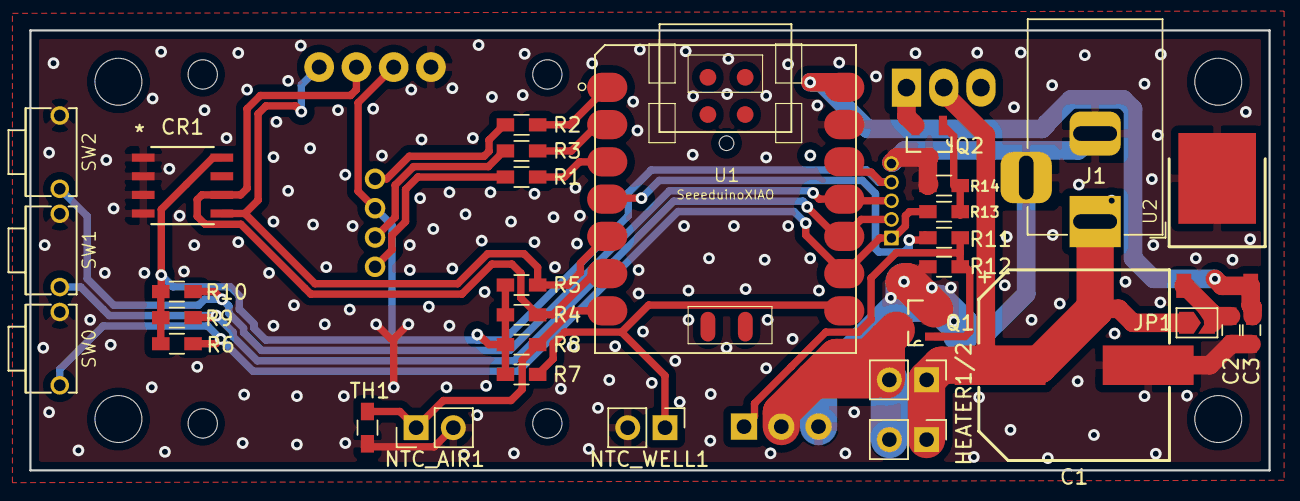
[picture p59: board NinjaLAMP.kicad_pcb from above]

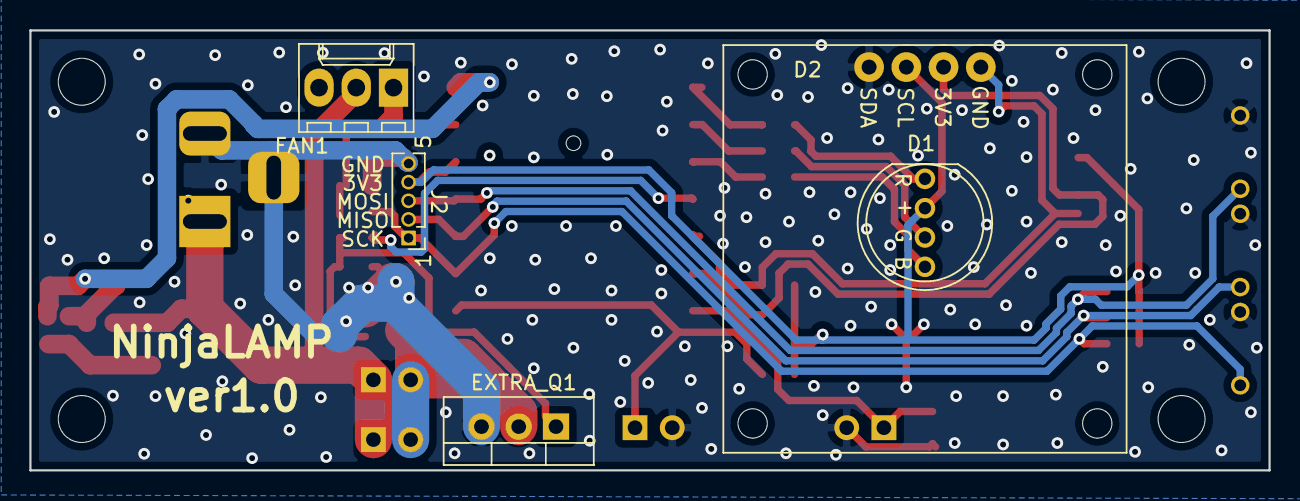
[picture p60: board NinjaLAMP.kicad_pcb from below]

Board: 2 copper layers, 84.5 x 30.0 mm, 37 parts (5 on the bottom side), 23 nets.

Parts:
C1: CP; ELECTRO-SMD-C-12.5x13.5MM
C2: 0.33uF; C_0603_HandSoldering
C3: 0.1uF; C_0603_HandSoldering
CR1: M24C02-RMN6TP
D1: DIP-LED-RGB-COMMON-ANODE_4P-D8MM_; LED4-2.0-D8.0MM
D2: I2C_SSD1306_LCD
EXTRA_Q1: BSP89; TO-220-3_Vertical
FAN1: Fan_3pin; Molex_KK-6410-03_03x2.54mm_Straight
HEATER1, HEATER2: Conn_01x02_Female; Pin_Header_Straight_1x02_Pitch2.54mm
J1: Barrel_Jack_Switch; BarrelJack_Horizontal
J2: Conn_01x05_Male; Pin_Header_Straight_1x05_Pitch1.27mm
JP1: Jumper; SolderJumper-2_P1.3mm_Open_TrianglePad1.0x1.5mm
NTC_AIR1: Conn_01x02_Female; Pin_Header_Straight_1x02_Pitch2.54mm
NTC_WELL1: Conn_01x02_Female; Pin_Header_Straight_1x02_Pitch2.54mm
Q1, Q2: BSP89; SOT95P240X112-3N
R1, R3: 15; R_0603_HandSoldering
R2: 75; R_0603_HandSoldering
R4, R5, R6, R7, R8, R9, R10, R12, R14: 47K; R_0603_HandSoldering
R11, R13: 1K; R_0603_HandSoldering
SW0, SW1, SW2: DIP-BUTTON_2P-6.0X3.0X4.3MM_; SW2-5.0-6.0X3.0X4.3MM
TH1: Thermistor; R_0603_HandSoldering
U1: SeeeduinoXIAO; SeeeduinoXIAO-MOUDLE14P-2.54-21X17.8MM
U2: PMIC-CJ78M05_TO-252_; TO-252

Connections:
+3V3: CR1.8, D1.3, D2.2, J2.4, R4.2, R5.2, R6.1, R7.1, R8.1, R9.1, R10.1, U1.12
+5V: C3.1, U1.14, U2.3
+12V: C1.1, FAN1.2, HEATER1.1, HEATER2.1, J1.1, JP1.1
/Q1: EXTRA_Q1.1, Q1.1, R11.1, R12.2
/Q2: EXTRA_Q1.2, HEATER1.2, HEATER2.2, Q1.3
AIN_AIR: NTC_AIR1.1, R8.2, TH1.1, U1.7
AIN_WELL: NTC_WELL1.1, R7.2, U1.8
GND: C1.2, C2.2, C3.2, CR1.1, CR1.2, CR1.3, CR1.4, D2.1, EXTRA_Q1.3, J1.2, J1.3, J2.5, NTC_AIR1.2, NTC_WELL1.2, Q1.2, Q2.3, R12.1, R14.1, SW0.2, SW1.2, SW2.2, TH1.2, U1.13, U2.2
HEATER: R11.2, U1.4
LED_B: R1.1, U1.3
LED_G: R3.1, U1.2
LED_R: R2.1, U1.1
unnamed: C2.1, JP1.2, U2.1
unnamed: D1.1, R1.2
unnamed: D1.2, R3.2
unnamed: D1.4, R2.2
unnamed: FAN1.1, Q2.2
unnamed: Q2.1, R13.1, R14.2
SCL: CR1.6, D2.3, R4.1, U1.6
SDA: CR1.5, D2.4, R5.1, U1.5
TACT0: J2.1, R6.2, R13.2, SW0.1, U1.9
TACT1: J2.2, R9.2, SW1.1, U1.10
TACT2: J2.3, R10.2, SW2.1, U1.11

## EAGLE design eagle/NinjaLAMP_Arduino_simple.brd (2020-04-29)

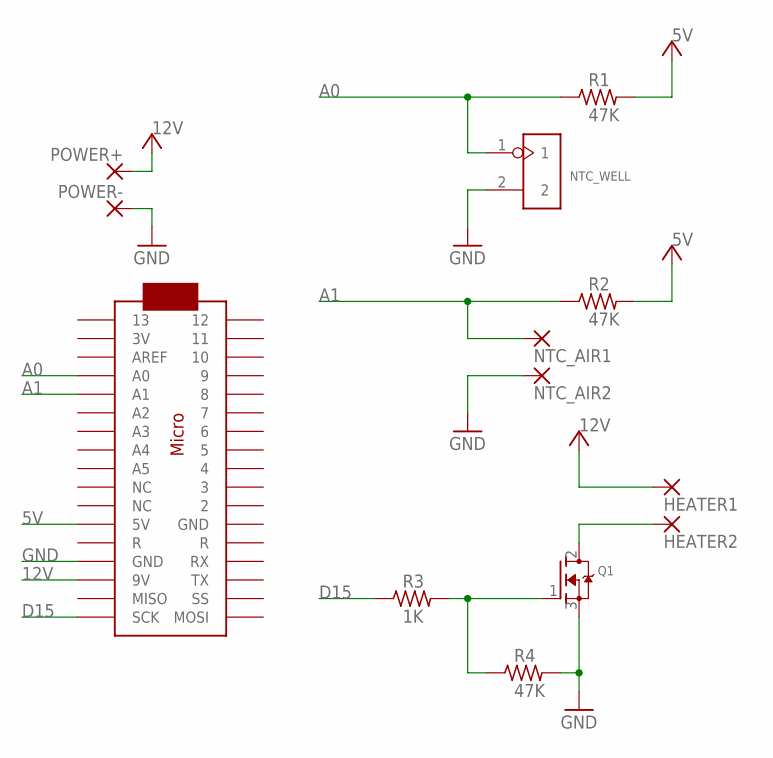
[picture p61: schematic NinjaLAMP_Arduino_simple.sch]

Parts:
HEATER1, HEATER2: 1,6/0,8
NTC_AIR1, NTC_AIR2: 1,6/0,8
NTC_WELL: 2p-2.54; H2-2.54
POWER+: 1,6/0,8
POWER-: 1,6/0,8
Q1: MOSFET-NGDS_TO220V; TO220V
R1, R2, R4: 47K; 0207/10
R3: 1K; 0207/10
U$1: ARDUINOMICRO

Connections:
5V: R1.2, R2.2, U$1.P$23 (5V)
12V: HEATER1.1, POWER+.1, U$1.P$20 (9V)
A0: NTC_WELL.1, R1.1, U$1.P$31 (A0)
A1: NTC_AIR1.1, R2.1, U$1.P$30 (A1)
D15: R3.1, U$1.P$18 (SCK)
DRAIN: HEATER2.1, Q1.2 (D)
GATE: Q1.1 (G), R3.2, R4.1
GND: NTC_AIR2.1, NTC_WELL.2, POWER-.1, Q1.3 (S), R4.2, U$1.P$12 (GND)

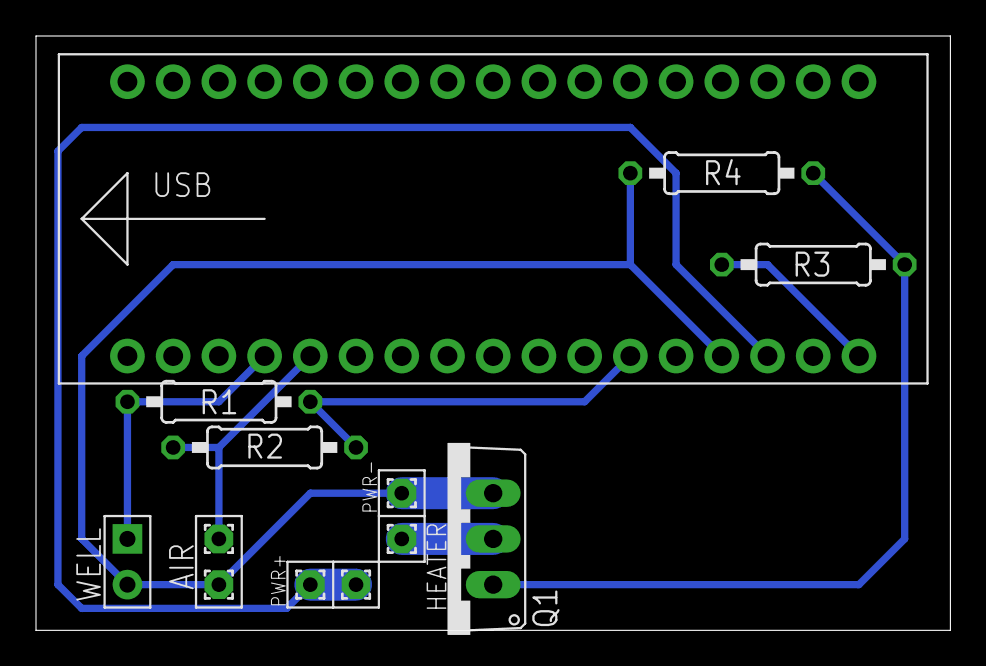
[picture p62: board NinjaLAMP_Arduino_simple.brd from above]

Board: 2 copper layers, 50.8 x 33.0 mm, 13 parts (0 on the bottom side), 8 nets.

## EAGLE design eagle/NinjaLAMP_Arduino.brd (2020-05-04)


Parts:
HEATER: 1X2-3.5MM
J1: 22-05-7038-03; 7395-03
JACK: DC-005; DCJ3P-14.2X11.0X9.0MM
LED: 2p-2.54; H2-2.54
NTC_AIR: 2p-2.54; H2-2.54
NTC_WELL: 2p-2.54; H2-2.54
Q1, Q2: MOSFET-NGDS_TO220V; TO220V
R1, R2, R4, R7: 47K; 0204/7
R3, R5, R6: 1K; 0204/7
U$2: ARDUINOMICRO

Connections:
5V: R1.2, R2.2, U$2.P$23 (5V)
12V: HEATER.1, J1.2, JACK.+B (+), JACK.+T (+), U$2.P$20 (9V)
A0: NTC_WELL.1, R1.1, U$2.P$31 (A0)
A1: NTC_AIR.1, R2.1, U$2.P$30 (A1)
D3: R6.1, U$2.P$10 (3)
D13: LED.1, U$2.P$34 (13)
D15: R3.1, U$2.P$18 (SCK)
DRAIN: HEATER.2, Q1.2 (D)
GATE: Q1.1 (G), R3.2, R4.1
GND: JACK.-1B (-), JACK.-1T (-), NTC_AIR.2, NTC_WELL.2, Q1.3 (S), Q2.3 (S), R4.2, R5.1, R7.2, U$2.P$12 (GND), U$2.P$21 (GND)
unnamed: LED.2, R5.2
unnamed: Q2.1 (G), R6.2, R7.1
unnamed: J1.3, Q2.2 (D)

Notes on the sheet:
EXTRA(NOT TESTED)
HEATER


Board: 2 copper layers, 46.0 x 33.0 mm, 16 parts (0 on the bottom side), 13 nets.

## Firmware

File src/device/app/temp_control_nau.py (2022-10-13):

#from adc_ADS1219IPWR import ADS1219
from adc_NAU7802 import NAU7802
from machine import Pin, PWM, SoftI2C
import math
import time
import pid
from pid import PIDRange, PID
from thermistor import Thermistor
from sample_temp_simulation import TempSimulation

print("pcr.py")
print("calling test_adc.start()")
adc_device_address = 42
scl = Pin(18, Pin.OUT, Pin.PULL_UP)
sda = Pin(5, Pin.OUT, Pin.PULL_UP)
i2c = SoftI2C(scl, sda, freq=80000)
# adc = ADS1219(i2c, adc_device_address, Pin(17, Pin.IN, Pin.PULL_UP))
adc = NAU7802(i2c, None, adc_device_address)
adc.start()

# S0=19, S1=21, S2=22, S3=23
mux_s0 = Pin(19, Pin.OUT)
mux_s1 = Pin(21, Pin.OUT)
mux_s2 = Pin(22, Pin.OUT)
mux_s3 = Pin(23, Pin.OUT)
well_heater_pin = Pin(25, Pin.OUT)
well_heater_pin.value(0)
well_heater = PWM(well_heater_pin, duty=0)

counter_r = 47
switch_val = 0
thermistor_ali = Thermistor(3950, 100, 25)
thermistor_nx = Thermistor(4311, 100, 25)
thermistor_aki = Thermistor(4250, 100, 25)
thermistor_none = Thermistor(4250, 100, 25)
# well, air, lid, ext1, ext2, ext3
thermistors = [thermistor_ali, thermistor_aki, thermistor_none, thermistor_nx, thermistor_none, thermistor_nx ]

# High/Low temp modes
therm_switch = Pin(27, Pin.OUT)

print("therm_switch")
therm_switch.value(switch_val)

selected_well = 0
well_count = 8
# adc.select_single_end_channel(1)
adc.select_analog_input_channel(1)
adc.select_conversion_rate(330)


sim = TempSimulation(temp_air=25, temp_well=25)

def select_mux (ch): 
    val0 = 0x01 & (ch >> 0)
    val1 = 0x01 & (ch >> 1)
    val2 = 0x01 & (ch >> 2)
    val3 = 0x01 & (ch >> 3)
    mux_s0.value(val0)
    mux_s1.value(val1)
    mux_s2.value(val2)
    mux_s3.value(val3)
print ("PCR 2022/05/25 11:07")

param_a = 0.35
param_b = 0.35
param_c = 15
param_d = 4

mux_ch_well = 0
mux_ch_air = 1

started = False
KELVIN = 273.15

resistance = 47
r0 = 100
baseTemp = 25
targetTemp = 100

range_low = PIDRange(kp=0.40, ki=0.035, kd=0.005, min_value=None, max_value=55)
range_mid = PIDRange(kp=0.40, ki=0.035, kd=0.005, min_value=55, max_value=80)
range_high = PIDRange(kp=0.4, ki=0.035, kd=0.005, min_value=80, max_value=None)
ranges = [range_low, range_mid, range_high]
pid = PID(ranges)
interval = 0.5
pid.set_interval(interval)
pid.set_output_range(0, 1.0)
TARGET_TEMP = 55
pid.set_setpoint(TARGET_TEMP)
time_zero = time.ticks_ms()

while True:
    # Measure well temp
    select_mux(mux_ch_well)
    temp_well = thermistors[mux_ch_well].to_temp(adc.read_conversion_data(), counter_r)
    # Measure air temp
    select_mux(mux_ch_air)
    temp_air = thermistors[mux_ch_air].to_temp(adc.read_conversion_data(), counter_r)
    sim.update(temp_air=temp_air, temp_well=temp_well)
    temp_sample = sim.simulate(interval=interval)
    pid.set_value(temp_well)
    
    output = pid.get_output()
    # duty = int(1023.0 * output)
    duty = int(128.0 * output)
    timestamp = time.ticks_ms() - time_zero
    # print("W=%.2f,A=%.2f,S=%.2f,%d,%.3f,%.3f,%.3f" % (temp_well,temp_air,temp_sample,duty,pid.p, pid.i, pid.d))
    print("T=%d\tW=%.2f\tA=%.2f\tO=%.2f" % (timestamp,temp_well,temp_air, output)) # Print timestamp
    well_heater.duty(duty)
    # well_heater.duty(0)
    
    time.sleep(interval)

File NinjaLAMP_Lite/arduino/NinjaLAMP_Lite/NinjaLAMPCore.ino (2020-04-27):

#include <PID_v1.h>
#include "adc_NAU7802.h"

/* Temperature COnfig */
#define TARGET_TEMP 63
#define MAX_OUTPUT_THRESHOLD 5

#define THERMISTOR_LOW_SIDE 1
#define THERMISTOR_HIGH_SIDE 2

/* Well */
const int wellThermistorRangeCount = 3;
struct ThermistorRange wellThermistorRanges[3] = {
  { 0.0, 4250, 0.0, },
  { 50.0, 4311, 0.0, },
  { 85.0, 4334, 0.0, },
};
const int WELL_THERMISTOR_PLACE = THERMISTOR_LOW_SIDE;
#define WELL_R_0 100.0 // R0
#define WELL_THERMISTOR_BASE_TEMP 25.0
// #define WELL_R 47 // Counter resistor (breadboard test)

#define WELL_R_SWITCHING
#ifdef WELL_R_SWITCHING
#define PIN_WELL_HIGH_TEMP 16
#define WELL_R_LOW 30 // Counter resistor (Low mode)
#define WELL_R_HIGH 10 // Counter resistor (High mode)
#define WELL_R_SWITCHING_TEMP 54
#else
#define WELL_R 30 // Counter resistor
#endif

#ifdef WELL_R_SWITCHING
double wellR = WELL_R_LOW;
void switchWellR (double temp) {
  double prevValue = wellR;
  if (temp > WELL_R_SWITCHING_TEMP) {
    wellR = WELL_R_HIGH;
    digitalWrite(PIN_WELL_HIGH_TEMP, HIGH);
  } else {
    wellR = WELL_R_LOW;
    digitalWrite(PIN_WELL_HIGH_TEMP, LOW);
  }
  if (wellR != prevValue) {
    calcVoltageLimits(wellThermistorRangeCount, wellThermistorRanges, wellR, WELL_R_0, WELL_THERMISTOR_BASE_TEMP);
  }
}
#else
double wellR = WELL_R;
#endif

/* Air */
const int airThermistorRangeCount = 3;
struct ThermistorRange airThermistorRanges[3] = {
  { 0.0, 4250, 0.0, },
  { 50.0, 4311, 0.0, },
  { 85.0, 4334, 0.0, },
};
const int AIR_THERMISTOR_PLACE = THERMISTOR_HIGH_SIDE;
#define AIR_R_0 100.0 // R0
#define AIR_THERMISTOR_BASE_TEMP 25.0
#define AIR_R 4.99 // Counter resistor
// #define AIR_R 47 // Counter resistor (breadboard test)

#define USE_EXTERNAL_ADC

/* Pinouts */
const int WELL_HEATER_PWM = 15;

/* Define analog input pins to use Arduino's AIN pins */
#ifndef USE_EXTERNAL_ADC
const int WELL_THERMISTOR_AIN = A0;
const int AIR_THERMISTOR_AIN = A1;
#endif

/* PID constants */
#define WELL_KP (0.11)
#define WELL_KI (0.5)
#define WELL_KD (2.0)

#define KELVIN 273.15
double setpoint, input, output;
// https://playground.arduino.cc/Code/PIDLibraryConstructor/
PID pid(&input, &output, &setpoint, WELL_KP, WELL_KI, WELL_KD, DIRECT);

#define INTERVAL_MSEC 250
#define TEMP_BUFF_SIZE 5
double tempBuff[TEMP_BUFF_SIZE];
int tempBuffIndex = 0;

double voltageToTemp (double voltageRatio, float resistance, float b_constant, float r0, double baseTemp) {
  double thermistorR = resistance * voltageRatio / (1.0 - voltageRatio);
  return (1 / ((log(thermistorR / r0) / b_constant) + (1.0 / (baseTemp + KELVIN))))  - KELVIN;
}

double tempToVoltageRatio (double tempCelsius, double resistance, double bConst, double r0, double baseTemp) {
  double thermistorR = r0 * exp(bConst * (1 / (tempCelsius + KELVIN) - 1 / (baseTemp + KELVIN)));
  return thermistorR / (thermistorR + resistance);
}
double averageTemp () {
  double tempSum = 0;
  for (int i=0; i<TEMP_BUFF_SIZE; i++) {
    tempSum += tempBuff[i];
  }
  return tempSum / TEMP_BUFF_SIZE;
}
  
double prev = 0;
double calcVoltageLimits (int rangeCount, ThermistorRange *ranges, double resistance, double r0, double baseTemp) {
  for (int i=1; i<rangeCount; i++) {
    ThermistorRange *range = &ranges[i];
    double vLimit = tempToVoltageRatio(range->tempLowerLimit, resistance, range->bConst, r0, baseTemp);
    range->voltageLimit = vLimit;
  }
}

void setupCore () {
  calcVoltageLimits(wellThermistorRangeCount, wellThermistorRanges, wellR, WELL_R_0, WELL_THERMISTOR_BASE_TEMP);
  calcVoltageLimits(airThermistorRangeCount, airThermistorRanges, AIR_R, AIR_R_0, AIR_THERMISTOR_BASE_TEMP);
  pinMode(WELL_HEATER_PWM, OUTPUT);
#ifdef WELL_R_SWITCHING
  pinMode(PIN_WELL_HIGH_TEMP, OUTPUT);
#endif
  input = readWellTemp();
  for (int i=0; i<TEMP_BUFF_SIZE; i++) {
    tempBuff[i] = input;
  }

#ifdef WELL_R_SWITCHING
  switchWellR(input);
#endif
  setpoint = TARGET_TEMP;
  pid.SetMode(MANUAL);
  pid.SetOutputLimits(-0.5, 0.5);
  pid.SetSampleTime(INTERVAL_MSEC);
  delay(INTERVAL_MSEC/2);
}


void loopCore () {
  loopCore();
  // Well temp
  double wellTempRaw = readWellTemp();
  tempBuff[tempBuffIndex] = wellTempRaw;
#ifdef WELL_R_SWITCHING
  switchWellR(wellTempRaw);
#endif
  tempBuffIndex = (tempBuffIndex + 1) % TEMP_BUFF_SIZE;
  double temp = averageTemp();
  if (temp < TARGET_TEMP - MAX_OUTPUT_THRESHOLD) {
    // Max drive
    analogWrite(WELL_HEATER_PWM, 1023);
    pid.SetMode(MANUAL);
  } else {
    // PID drive
    input = temp;
    pid.SetMode(AUTOMATIC);
    pid.Compute();
    double pwmOutput = (output + 0.5) * 408/*1024*/;
    analogWrite(WELL_HEATER_PWM, (int)pwmOutput);
  }
  // TODO: switch high/low resistors if needed
  delay(INTERVAL_MSEC/2);

  // Air temp
  double airTemp = readAirTemp();
  Serial.print(airTemp);
  Serial.print("\t");
  Serial.println(temp);
  delay(INTERVAL_MSEC/2);  
}


/* Read analog value */
double readWellThermistorVoltageRatio () {
#ifdef USE_EXTERNAL_ADC
  float voltageRatio;
  HardwareStatus result = getWellADCValue(&voltageRatio);
  return voltageRatio;
#else
  return analogRead(WELL_THERMISTOR_AIN) / 1024.0;
#endif
}

double readAirThermistorVoltageRatio () {
#ifdef USE_EXTERNAL_ADC
  float voltageRatio;
  HardwareStatus result = getLidADCValue(&voltageRatio);
  return voltageRatio;
#else
  return analogRead(AIR_THERMISTOR_AIN) / 1024.0;
#endif
  
}

double bConstantForVoltage (int rangeCount, ThermistorRange *ranges, double voltageRatio) {
  float bConstant = ranges[0].bConst;
  for (int i=1; i<rangeCount; i++) {
    ThermistorRange *range = &ranges[i];
    if (voltageRatio < range->voltageLimit) {
      bConstant = range->bConst;
    }
  }
  return bConstant;
}

double readWellTemp () {
  double wellVoltage = readWellThermistorVoltageRatio();
#if WELL_THERMISTOR_PLACE==THERMISTOR_LOW_SIDE
  double voltageRatio = wellVoltage;
#else
  double voltageRatio = 1.0 - wellVoltage;
#endif
  float bConstant = bConstantForVoltage(wellThermistorRangeCount, wellThermistorRanges, voltageRatio);
  return voltageToTemp(voltageRatio, wellR, bConstant, WELL_R_0, WELL_THERMISTOR_BASE_TEMP);
}

double readAirTemp () {
  double airVoltage = readAirThermistorVoltageRatio();
#if AIR_THERMISTOR_PLACE==THERMISTOR_LOW_SIDE
  double voltageRatio = airVoltage;
#else
  double voltageRatio = 1.0 - airVoltage;
#endif
  float bConstant = bConstantForVoltage(airThermistorRangeCount, airThermistorRanges, voltageRatio);
  return voltageToTemp(voltageRatio, AIR_R, bConstant, AIR_R_0, AIR_THERMISTOR_BASE_TEMP);
}

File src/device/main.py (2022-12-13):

import time
import network
from wifi_config import preferred_aps, network_state
from machine import Pin, SoftI2C
import os

print("HEATER ZERO")
from machine import Pin
Pin(25, Pin.OUT).value(0) # Well heater off

wlan = network.WLAN(network.STA_IF)
network_state["wlan"] = wlan
wlan.active(True)

connection_interval = 0.1
connection_timeout = 5.0


def try_connection (target, config):
    delay = 0
    print("Trying to connect...")
    print(target)
    wlan.connect(config[0], config[1]) # SSID, password
    while not wlan.isconnected() :
        time.sleep(connection_interval)
        delay += connection_interval
        if delay > connection_timeout:
            print("Timeout.")
            wlan.disconnect()
            return None # Failed
    # Return wlan config
    return wlan.ifconfig()


def connect ():
    # Scan
    print("Scanning...")
    aps = wlan.scan()
    # (ssid, bssid, channel, RSSI, security, hidden)
    # Sort by RSSI ([3])
    sorted_ap = sorted(aps, key=lambda x: x[3], reverse=True)
    for found in sorted_ap:
        for preferred in preferred_aps:
            # Compare
            if (preferred[0] == found[0].decode("utf-8") ):
                result = try_connection(found, preferred)
                if result is not None:
                    print("Connected.")
                    print(result)
                    return True
    return False


if "conf" not in os.listdir():
    print("Creating conf dir")
    os.mkdir("conf")
if "certs" not in os.listdir():
    print("Creating certs dir")
    os.mkdir("certs")


pin_ap_mode=Pin(33, Pin.IN, Pin.PULL_UP)
pin_no_run=Pin(2, Pin.IN, Pin.PULL_UP)
PIN_VALUE_ON = 0

def lcd_message (msg0, msg1):
    import ssd1306 #LCD
    lcd_device_address = 64
    scl = Pin(12, Pin.OUT, Pin.PULL_UP)
    sda = Pin(13, Pin.OUT, Pin.PULL_UP)
    i2c = SoftI2C(scl, sda, freq=80000)
    lcd = ssd1306.SSD1306_I2C(128, lcd_device_address, i2c)
    lcd.fill(1)
    lcd.text(msg0, 2, 2, 0)
    lcd.text(msg1, 2, 16, 0)
    lcd.show()

def ap_mode ():
    ap = network.WLAN(network.AP_IF)
    ap.active(False)
    ap.active(True)
    ap.config(essid="qNinjaLITE")
    lcd_message("AP Mode",ap.ifconfig()[0])

print([pin_ap_mode.value(), pin_no_run.value()])

if pin_ap_mode.value()==PIN_VALUE_ON:
    print("Boot in AP mode")
    ap_mode()
else:
    if connect():    
        print("WiFi Client Mode")
        if pin_no_run.value()==PIN_VALUE_ON:
            print("No MQTT")
            lcd_message("WLAN Mode",wlan.ifconfig()[0])
        else:
            print("Start MQTT")
            #try:
            import cycler_mqtt
            #except :
                #print("Import error")
    else:
        print("Connection failed")
        ap_mode()

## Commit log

2020-04-24 Add Arduino code (With built-in ADC)
2020-04-25 add 3d model and dxf
    [NinjaLAMP-Lite-t5.5mm ver1.0 v13.step, w1_body-right.dxf, w2_body-back.dxf, w3_body-bottom.dxf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]
2020-04-25 Remove unused constants / Support 2 types of thermistor & resistor placing
2020-04-26 add pcb infomation
2020-04-26 Resistor switching
2020-04-27 Move source files into arduino folder
2020-04-27 Add arduino project dir for Lite edition
2020-04-27 Customization for Arduino edition (Remove WiFi features / Remove external ADCs)
2020-04-27 update 3d model of Lite
    [NinjaLAMP-Lite-t5.5mm ver1.0 v13.step, NinjaLAMP-Lite-t5.5mm ver1.0 v21.step, w1_body-right.dxf, w2_body-back.dxf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]
2020-04-27 Receive target temperature at "/start"
2020-04-27 add stl data for Lite
    [3d-2x8-kit_body.stl, 3d-2x8-maker_body.stl, 3d-2x8_well-holder.stl, 3d-4x4-kit_body.stl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]
2020-04-28 add eagle files
    [NinjaLAMP_Arduino.brd, NinjaLAMP_Arduino.sch]
2020-04-28 Move definition of PWM pin to the top
2020-04-28 add 3d stl
    [4x4_3dprint.stl]
2020-04-29 Add image of "upload" button on Arduino IDE
2020-04-29 Add screenshot of Arduino serial monitor
2020-04-29 update 3d model : add cover
    [4x4_3d_base.stl, 4x4_3d_cover.stl, 4x4_3dprint.stl, NinjaLAMP-Lite-t5.5mm ver1.0 v33.step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]
2020-04-30 add cover
    [4x4_3d_base.stl, 4x4_3d_cover.stl]
2020-04-30 add belt
    [4x4_3d_belt.stl, 4x4_3d_cover.stl]
2020-05-01 Add illustration of heat simulation feature
2020-05-01 Add images (to illustrate how to use Arduino IDE's serial UI)
2020-05-02 Arduino version become de fact NinjaLAMP
    [3d-2x8-kit_body.stl, 3d-2x8-maker_body.stl, 3d-2x8_well-holder.stl, 3d-4x4-kit_body.stl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]
2020-05-02 Add images of Arduino's library manager
2020-05-02 Support multiple stages
2020-05-03 Add a link to "Experiments with multiple stages" article
2020-05-04 t5.5 lasercut design finished
    [3d-2x8-kit_body.stl, 3d-2x8-maker_body.stl, 3d-2x8_well-holder.stl, 3d-4x4-kit_body.stl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]
2020-05-05 add simple lasercut model with t6.0mm
    [sw1-t6_body-top.dxf, sw2-t6_cover-top.dxf, sw3-t6_cover-front.dxf, sw4-t6_cover-left.dxf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]
2020-05-16 add simple pcb
    [NinjaLAMP_Arduino_simple.brd, NinjaLAMP_Arduino_simple.sch]
2020-05-20 add 3d model of tube_holder
    [tube_holder.f3d, tube_holder.iges, tube_holder.step, tube_holder.stl]
2020-10-28 pcb ver1.0 complete
    [NinjaLAMP.kicad_pcb, NinjaLAMP.sch, NinjaLAMP.step]
2020-10-29 added tacts and EEPROM
    [NinjaLAMP-BOM.csv, NinjaLAMP.kicad_pcb, NinjaLAMP.sch]
2020-10-30 added 1x8 and 2x8 iges
    [BOM.xlsx, NinjaLAMP-BOM.csv, NinjaLAMP.csv, NinjaLAMP.kicad_pcb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]
2020-11-06 add 3dprint data
    [3dprint_1x8_bottom.stl, 3dprint_1x8_cover.stl, 3dprint_2x8_bottom.stl, 3dprint_2x8_cover.stl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]
2020-11-10 bigger footprint for polcap
    [NinjaLAMP.kicad_pcb]
2020-11-10 add todo memo
    [NinjaLAMP.kicad_pcb]
2020-11-11 correct MOSFET pins
    [NinjaLAMP-B_Cu.gbl, NinjaLAMP-B_Mask.gbs, NinjaLAMP-B_Paste.gbp, NinjaLAMP-B_SilkS.gbo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]
2020-11-13 add pdf and images of ver1.0 kicad
    [BOM.xlsx, NinjaLAMP.csv, NinjaLAMP.kicad_pcb, NinjaLAMP.sch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]
2020-11-25 restored sample items
2022-03-03 just before import netlist to qLAMP-main-2x8
    [file-1V.kicad_sch, file12V_UPS.kicad_sch, file3V3.kicad_sch, file5V_UPS.kicad_sch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]
2022-03-07 dru cleared
    [file-1V.kicad_sch, file12V_UPS.kicad_sch, file3V3.kicad_sch, file5V_UPS.kicad_sch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]
2022-03-07 just before placing vias
    [qLAMP-main.kicad_pcb]
2022-03-07 batch01 ready
    [qLAMP-lcd-B_Cu.gbr, qLAMP-lcd-B_Mask.gbr, qLAMP-lcd-B_Paste.gbr, qLAMP-lcd-B_Silkscreen.gbr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]
2022-03-09 changing pd and demodulator
    [photo-single-B_Cu.gbl, photo-single-B_Mask.gbs, photo-single-B_Paste.gbp, photo-single-B_Silkscreen.gbo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]
2022-03-10 prepare batch02/main with todo comments
    [file-1V.kicad_sch, file12V_UPS.kicad_sch, file3V3.kicad_sch, file5V_UPS.kicad_sch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]
2022-06-09 ordered batch2/main
    [filePhoto.kicad_sch, filePhotoMUX.kicad_sch, filePhotoThermistors.kicad_sch, filePower.kicad_sch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]
2022-06-12 put latest well
    [tube_holder.f3d, tube_holder.iges, tube_holder.step, tube_holder.stl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]
2022-06-13 move dirs as qNinja
    [1x8_body_top.dxf, 1x8_pcb_south.dxf, 2x8_body_top.dxf, 3dprint_1x8_bottom.stl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]
2022-06-13 move dirs unused anymore
    [NinjaLAMP_Arduino.brd, NinjaLAMP_Arduino.sch, NinjaLAMP_Arduino_simple.brd, NinjaLAMP_Arduino_simple.sch]
2022-06-16 initialize batch03/main
    [file-1V.kicad_sch, file12V_UPS.kicad_sch, file3V3.kicad_sch, file5V_UPS.kicad_sch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]
2022-06-26 add batch03 and batch02/pdf
    [filePhotoThermistors.kicad_sch, filePower.kicad_sch, qLAMP-main.kicad_pcb, qLAMP-main.kicad_sch]
2022-08-12 just before ripup batch03/main
    [filePhotoMUX.kicad_sch, filePhotoThermistors.kicad_sch, filePower.kicad_sch, photo-single-B_Cu.gbl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]
2022-08-12 wiring batch03/main
    [filePhoto.kicad_sch, filePhotoLED.kicad_sch, filePhotoThermistors.kicad_sch, qLAMP-main.kicad_pcb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]
2022-08-14 wiring batch03/main done
    [filePhotoThermistors.kicad_sch, qLAMP-main.kicad_pcb, qLAMP-main.kicad_sch]
2022-08-14 batch03 finished
    [file-1V.kicad_sch, file12V_UPS.kicad_sch, file3V3.kicad_sch, file5V_UPS.kicad_sch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]
2022-08-15 add pads below all pds
    [filePhotoMUX.kicad_sch, filePhotoThermistors.kicad_sch, qLAMP-main-B_Cu.gbl, qLAMP-main-B_Mask.gbs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]
2022-08-17 add reg alt
    [filePhotoThermistors.kicad_sch, filePower.kicad_sch, qLAMP-main.kicad_pcb, qLAMP-main.kicad_sch]
2022-10-06 wiring batch04/main
    [file-1V.kicad_sch, file12V_UPS.kicad_sch, file3V3.kicad_sch, file5V_UPS.kicad_sch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]
2022-10-13 ordered batch04
    [filePhotoThermistors.kicad_sch, qLAMP-lcd-B_Cu.gbr, qLAMP-lcd-B_Mask.gbr, qLAMP-lcd-B_Paste.gbr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]
2022-10-18 init batch05
    [file-1V.kicad_sch, file12V_UPS.kicad_sch, file3V3.kicad_sch, file5V_UPS.kicad_sch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]
2022-10-26 Enable & disable buttons according to the device state
2022-10-27 update dxf
    [1x8_body_top.dxf, 1x8_pcb_south.dxf, 2x8_body_top.dxf, body_back.dxf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]
2022-11-07 wired batch05/main
    [filePhotoLED.kicad_sch, filePhotoThermistors.kicad_sch, qLAMP-lcd-B_Cu.gbr, qLAMP-lcd-B_Mask.gbr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]
2022-11-08 thick holder to remove washers
    [RubberHolder1x8.stl]
2022-11-28 Use topic filter "aws/#"
2022-12-01 Fixed scrolling bug of temperature chart
2022-12-02 quote paths
    [pd-cover-5.09x4-simple.stl]
2022-12-04 Workaround for the updated device status logic
2022-12-05 Use device presence API
    * Replace ping logic with presence API
    * Add JSON/CSV button to progress monitor
2022-12-13 Update sample usage of deploy.sh
2023-01-17 ordered b6
    [file-1V.kicad_sch, file12V_UPS.kicad_sch, file3V3.kicad_sch, file5V_UPS.kicad_sch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]
2023-02-10 add batch7
    [file-1V.kicad_sch, file12V_UPS.kicad_sch, file3V3.kicad_sch, file5V_UPS.kicad_sch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]
2023-02-24 wiring batch7
    [filePhotoLED.kicad_sch, filePhotoMUX.kicad_sch, filePhotoThermistors.kicad_sch, filePower.kicad_sch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]
2023-02-28 wiring batch7 main
    [filePhotoThermistors.kicad_sch, qLAMP-main-B_Cu.gbl, qLAMP-main-B_Mask.gbs, qLAMP-main-B_Paste.gbp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]
2023-03-12 modeling ver0.4 complete
    [1x8_body_top.dxf, 1x8_pcb_south.dxf, 2x8_body_top.dxf, body_back.dxf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]
2023-03-13 add 3d model of stl-ver0.4
    [RubberHolder1x8.stl, case_lowerA.stl, case_lowerB.stl, innerCase_1x8.stl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]
2023-04-27 soldered batch07/main
    [file-1V.kicad_sch, file12V_UPS.kicad_sch, file3V3.kicad_sch, file5V_UPS.kicad_sch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]

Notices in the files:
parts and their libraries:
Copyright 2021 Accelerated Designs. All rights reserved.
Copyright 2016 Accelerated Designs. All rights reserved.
